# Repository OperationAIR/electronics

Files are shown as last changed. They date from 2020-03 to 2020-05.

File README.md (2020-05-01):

# Electronics and firmware for Operation Air Ventilator

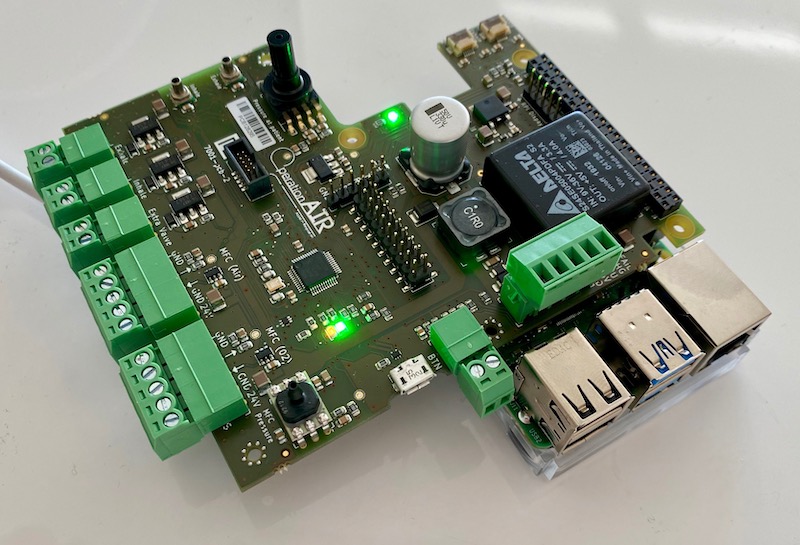
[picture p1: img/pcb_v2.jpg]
OperationAir PCB


The electronics for the Operation Air AIROne is comprised of a custom developed PCB with a LPC11U37 microcontroller stacked on top of a Raspberry Pi 4 (Model B).

This repository contains the electronic designs for the PCB and the accompanying firmware.

The Pi talks to the microcontroller over UART using a [custom binary protocol](firmware/README.md#uart-communication-protocol).

Contact info@interay.com for assembled, tested and programmed ready for use boards.

## License

Copyright (c) 2020 TU Delft. All rights reserved.

Licensed under the [Apache 2.0](LICENSE) license.

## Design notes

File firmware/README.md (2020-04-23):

# Operation Air embedded firmware

The firmware runs on a LPC11U37 microcontroller.

## Requirements

* [Gnu Arm Embedded Toolchain](https://developer.arm.com/open-source/gnu-toolchain/gnu-rm/downloads)
* CMake
* JTAG/SWD programmer, such as the [Black Magic Probe](https://github.com/blacksphere/blackmagic/wiki) (BMP) , or any OpenOCD compatible device.

## Build

First we need to create a `config.cmake` file in which we can configure our build

```console
cp config.cmake.example config.cmake
```

In `config.cmake` we can configure the BMP if we're using any. On MacOS that would look like:

```
set(BLACKMAGIC_DEV /dev/cu.usbmodemC1DDCDF81)
```

Next we need to create a `build` directory in the project root and run CMake to fetch all dedpendencies and create the makefiles.

```console
mkdir build
cd build
cmake ..
```

The previous part only needs to be done the first time.
Now we're ready to actually compile the project. Inside the `build` directory run

```console
make
```

And to flash

```console
make flash
```

## UART Communication Protocol

The microcontroller communicates with a Raspberry Pi over `uart`. The PCB is designed as a Raspberry Pi Hat and uses the `TXD` and `RXD` pins in the Raspberry Pi header. Note that `Rx` and `Tx` are swapped on the microcontroller side.

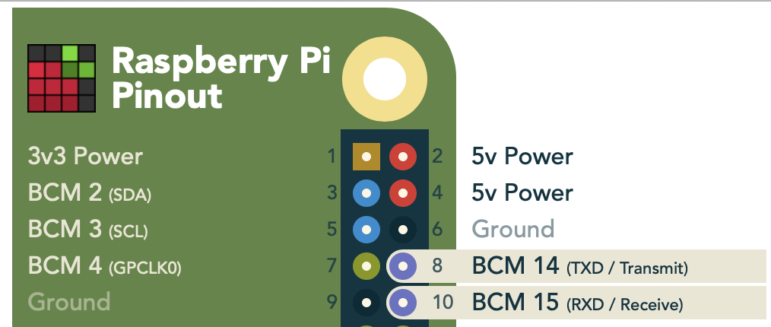
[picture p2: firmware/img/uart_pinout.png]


A binary protocol is used where each command is a unique 32 bit integer (sent LSB first) followed by an optional payload.

The baudrate is `500000`.

Binary responses from the microcontroller for the specific command are also prefixed with the same 4 bytes. ASCII responses, for logging or debug puposes are prefixed with `0x23232323` ('####') and end in a newline `\n` character.

### Command Overview

| Command             | Description                             | Prefix     | Payload      | Response         |
| -------------       |---------------------------------------- | ---------: | ------------ | --------         |
| NewSettings         | Send and apply new operation settings   | `0x41424344` | [Settings](#Settings)   | Applied Settings |
| RequestSettings     | Request current settings                | `0x45464748` | None         | [Settings](#Settings-Response) |
| RequestSensorValues | Request current samples for all sensors | `0x0D15EA5E` | None         | [Sensor Values](#Sensor-Values-Response)    |
| InspiratoryHoldStart| Trigger inspiratory hold if breathing is started | `0x99998888` | None| Log info (ascii) |
| InspiratoryHoldStop | Stop inspiratory hold                   | `0x99999999` | None         | Log info (ascii) |
| ExpiratoryHoldStart | Trigger expiratory hold if breathing is started | `0x77776666` | None | Log info (ascii) |
| ExpiratoryHoldStop  | Stop expiratory hold                    | `0x77777777` | None         | Log info (ascii) |
| StatusLedOn         | Turn on status LED (Green)              | `0x55551111` | None         | Log info (ascii) |
| StatusLedOff        | Turn off status LED (Green)             | `0x55661111` | None         | Log info (ascii) |
| ErrorLedOn          | Turn on error LED (Red)                 | `0x55552222` | None         | Log info (ascii) |
| ErrorLedOff         | Turn off error LED (Red)                | `0x55662222` | None         | Log info (ascii) |
| SwitchExhaleOn      | Turn on 24V switch for exhale           | `0x66663333` | None         | Log info (ascii) |
| SwitchExhaleOff     | Turn off 24V switch for exhale          | `0x66773333` | None         | Log info (ascii) |
| SwitchInhaleOn      | Turn on 24V switch for inhale           | `0x66664444` | None         | Log info (ascii) |
| SwitchInhaleOff     | Turn off 24V switch for ihale           | `0x66774444` | None         | Log info (ascii) |
| SwitchExtraOn       | Turn on 24V switch (extra)              | `0x66665555` | None         | Log info (ascii) |
| SwitchExtraOff      | Turn off 24V switch (extra)             | `0x66775555` | None         | Log info (ascii) |
| MFCAirSet           | Set 12 bit analog value for MFC (Air)   | `0x77771111` | [uint16 (mV)](#MFC-set-point) | Log info (ascii) |
| MFCAirGet           | Get analog MFC (Air) feedback value     | `0x77881111` | None         | [MFC Feedback uint16 (mV)](#MFC-analog-in)  |
| MFCO2Set            | Set 12 bit analog value for MFC (O2)    | `0x77772222` | [uint16 (mV)](#MFC-set-point) | Log info (ascii) |
| MFCO2Get            | Get analog MFC (O2) feedback value      | `0x77882222` | None         | [MFC Feedback uint16 (mV)](#MFC-analog-in)  |
| UserSwitchGet       | Get current user switch status (0 or 1) | `0x88883333` | None         | 0 or 1 (ascii)   |

### Settings

Settings is defined as a struct where each entry is a 16 bit unsigned integer.

```
typedef struct __attribute__((packed)) {
    uint16_t start; // breathing is started
    uint16_t peep; // exhale pressure
    uint16_t frequency; // breathing cycles per minute
    uint16_t ratio; // ratio between inhale exhale
    uint16_t pressure; // inhale pressure
    uint16_t oxygen; // oxygen percentage for mixer
    uint16_t max_pressure_alarm;
    uint16_t min_pressure_alarm;
    uint16_t max_TV_alarm;
    uint16_t min_TV_alarm;
    uint16_t max_fiO2_alarm;
    uint16_t min_fiO2_alarm;
    uint16_t crc;
} OperationSettings;
```

The final entry is a `crc16 usb` checksum with the following specs:

```
CRC16 USB
Poly: 0x8005
Init: 0xFFFF
RefIn: True
RefOut: True
XorOut: 0xFFFF
```

### Sensor Values Response

From microcontroller to host.
Sensor values are prefixed with the 32-bit little-endian value `0x0D15EA5E` and followed by a crc16 usb checksum. The sensor data is a struct of 32bit signed integers:

The total data packet is then `4 + (15 x 4) + 2 = 66 bytes`

```
struct SensorsAllData {
    int32_t flow_inhale;            // Inhale flow [mL / minute] (approximation)
    int32_t flow_exhale;            // Exhale flow [mL / minute]

    int32_t pressure_inhale;        // Inhale pressure [Pa]
    int32_t pressure_exhale;        // Exhale pressure [Pa]
    int32_t pressure_patient;       // Pressure at patient [Pa] (TODO: Not Implemented Yet)
    int32_t pressure_mfc;           // Pressure at MFC pressure vessel [Pa]

    int32_t oxygen;                 // Oxygen percentage [0-100]
    int32_t tidal_volume_inhale;    // Tidal volume [mL] (Based on inhale flow)
    int32_t tidal_volume_exhale;    // Tidal volume [mL] (Based on exhale flow)
    int32_t minute_volume;          // Average flow (exhale) [mL / minute] (average over last 10 sec interval)
    int32_t cycle_state;            // PeeP / Peak / None
    int32_t power_status;           // UPS status [mV OR-ed with UPSStatus bits]

    int32_t inspiratory_hold_result;// Value for end of inspiratory hold mean sensors
    int32_t expiratory_hold_result; // Value for end of expiratory hold mean sensors

    uint32_t system_status;         // enum SystemStatus value(s) OR-ed together

}
```

The power_status field shows the measured power voltage in mv, OR-combined with one
of these status flags:
```
enum UPSStatus {
    UPS_STATUS_UNKNOWN              = (0),
    UPS_STATUS_OK                   = (1 << 31),
    UPS_STATUS_BATTERY_POWERED      = (1 << 30),
    UPS_STATUS_FAIL                 = (1 << 29)
};

```

The system_status field shows multiple OR-combined flags indicating the status
of the electronics, including errors that have occurred. In normal operation,
only the flag `SYSTEM_STATUS_BOOT_POWER_ON` (or `SYSTEM_STATUS_BOOT_RESET_BY_PI` after a firmware upgrade) is expected to be set. Flags are only cleared by a resetting the MCU: a flag being set means that the error has occurred at least once since the last reset.
```
enum SystemStatus {
    SYSTEM_STATUS_UNKNOWN               = 0,

    // Boot info: one of these should be set at boot
    SYSTEM_STATUS_BOOT_POWER_ON         = (1 << 0),     // Power-On-Reset
    SYSTEM_STATUS_BOOT_RESET_BY_PI      = (1 << 1),     // External reset (triggered by RPI)
    SYSTEM_STATUS_BOOT_RESET_BY_ERROR   = (1 << 2),     // Watchdog reset (firmware bug)
    SYSTEM_STATUS_BOOT_RESET_BY_PWR_FAIL= (1 << 3),     // BOD reset (3.3V unstable)
    SYSTEM_STATUS_BOOT_RESET_BY_UNKNOWN = (1 << 4),     // SYSRST or unknown

    // Errors in sensors or actuators:
    SYSTEM_STATUS_ERROR_SENSOR_P_INSP   = (1 << 5),     // Inspiration pressure sensor error
    SYSTEM_STATUS_ERROR_SENSOR_P_EXP    = (1 << 6),     // Expiration pressure sensor error
    SYSTEM_STATUS_ERROR_SENSOR_P_PATIENT= (1 << 7),     // Patient pressure sensor error
    SYSTEM_STATUS_ERROR_SENSOR_FLOW     = (1 << 8),     // Flow sensor error

    SYSTEM_STATUS_ERROR_ACTUATOR_MFC_AIR= (1 << 16),    // Air MFC (DAC) error
    SYSTEM_STATUS_ERROR_ACTUATOR_MFC_O2 = (1 << 17),    // O2 MFC (DAC) error

    SYSTEM_STATUS_ERROR_MFC_OVERPRESSURE= (1 << 18),    // MFC output pressure too high

    // NOTE: new status flags may be added here
    //

    // Generic errors
    SYSTEM_STATUS_ERROR_EEPROM          = (1 << 29),    // EEPROM error: settings may not be remembered after reset
    SYSTEM_STATUS_ERROR_I2C_BUS         = (1 << 30),    // I2C bus is in invalid state

    // Warning: the firmware is not a release build
    SYSTEM_STATUS_DEBUG_ENABLED         = (1 << 31),    // Debug build should not be released
};

```

### Settings Response

From microcontroller to host.
Settings are prefixed with the 32-bit little-endian value: `0x41424344`, followed by the [Settings](#Settings).

### MFC set point

Set point for the mass flow controller. The MFC is controlled through a 12bit i2c DAC. The payload for the MFC set command accepts a unsigned 16 bit integer between 0 and 4095.

### MFC analog in

Feedback from the MFC are returned as uint16 value in millivolts (0-5000). Note: this command is binary and is not terminated with '\n'.

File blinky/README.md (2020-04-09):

# Operation Air embedded firmware

The firmware runs on a LPC11U37 microcontroller.

## Requirements

* [Gnu Arm Embedded Toolchain](https://developer.arm.com/open-source/gnu-toolchain/gnu-rm/downloads)
* CMake
* JTAG/SWD programmer, such as the [Black Magic Probe](https://github.com/blacksphere/blackmagic/wiki) (BMP) , or any OpenOCD compatible device.

## Build

First we need to create a `config.cmake` file in which we can configure our build

```console
cp config.cmake.example config.cmake
```

In `config.cmake` we can configure the BMP if we're using any. On MacOS that would look like:

```
set(BLACKMAGIC_DEV /dev/cu.usbmodemC1DDCDF81)
```

Next we need to create a `build` directory in the project root and run CMake to fetch all dedpendencies and create the makefiles.

```console
mkdir build
cd build
cmake ..
```

The previous part only needs to be done the first time.
Now we're ready to actually compile the project. Inside the `build` directory run

```console
make
```

And to flash

```console
make flash
```

## UART Communication Protocol

The microcontroller communicates with a Raspberry Pi over `uart`. The PCB is designed as a Raspberry Pi Hat and uses the `TXD` and `RXD` pins in the Raspberry Pi header. Note that `Rx` and `Tx` are swapped on the microcontroller side.



A binary protocol is used where each command is a unique 32 bit integer (sent LSB first) followed by an optional payload.

The baudrate is `500000`.

Binary responses from the microcontroller for the specific command are also prefixed with the same 4 bytes. ASCII responses, for logging or debug puposes are prefixed with `0x23232323` ('####') and end in a newline `\n` character.

### Command Overview

| Command             | Description                             | Prefix     | Payload      | Response         |
| -------------       |---------------------------------------- | ---------: | ------------ | --------         |
| NewSettings         | Send and apply new operation settings   | `0x41424344` | [Settings](#Settings)   | Applied Settings |
| RequestSettings     | Request current settings                | `0x45464748` | None         | [Settings](#Settings-Response) |
| RequestSensorValues | Request current samples for all sensors | `0x0D15EA5E` | None         | [Sensor Values](#Sensor-Values-Response)    |
| InspiratoryHoldStart| Trigger inspiratory hold if breathing is started | `0x99998888` | None| Log info (ascii) |
| InspiratoryHoldStop | Stop inspiratory hold                   | `0x99999999` | None         | Log info (ascii) |
| ExpiratoryHoldStart | Trigger expiratory hold if breathing is started | `0x77776666` | None | Log info (ascii) |
| ExpiratoryHoldStop  | Stop expiratory hold                    | `0x77777777` | None         | Log info (ascii) |
| StatusLedOn         | Turn on status LED (Green)              | `0x55551111` | None         | Log info (ascii) |
| StatusLedOff        | Turn off status LED (Green)             | `0x55661111` | None         | Log info (ascii) |
| ErrorLedOn          | Turn on error LED (Red)                 | `0x55552222` | None         | Log info (ascii) |
| ErrorLedOff         | Turn off error LED (Red)                | `0x55662222` | None         | Log info (ascii) |
| SwitchExhaleOn      | Turn on 24V switch for exhale           | `0x66663333` | None         | Log info (ascii) |
| SwitchExhaleOff     | Turn off 24V switch for exhale          | `0x66773333` | None         | Log info (ascii) |
| SwitchInhaleOn      | Turn on 24V switch for inhale           | `0x66664444` | None         | Log info (ascii) |
| SwitchInhaleOff     | Turn off 24V switch for ihale           | `0x66774444` | None         | Log info (ascii) |
| SwitchExtraOn       | Turn on 24V switch (extra)              | `0x66665555` | None         | Log info (ascii) |
| SwitchExtraOff      | Turn off 24V switch (extra)             | `0x66775555` | None         | Log info (ascii) |
| MFCAirSet           | Set 12 bit analog value for MFC (Air)   | `0x77771111` | [uint16 (mV)](#MFC-set-point) | Log info (ascii) |
| MFCAirGet           | Get analog MFC (Air) feedback value     | `0x77881111` | None         | [MFC Feedback (mV)](#MFC-analog-in)  |
| MFCO2Set            | Set 12 bit analog value for MFC (O2)    | `0x77772222` | [uint16 (mV)](#MFC-set-point) | Log info (ascii) |
| MFCO2Get            | Get analog MFC (O2) feedback value      | `0x77882222` | None         | [MFC Feedback (mV)](#MFC-analog-in)  |
| UserSwitchGet       | Get current user switch status (0 or 1) | `0x88883333` | None         | 0 or 1 (ascii)   |

### Settings

Settings is defined as a struct where each entry is a 16 bit unsigned integer.

```
typedef struct __attribute__((packed)) {
    uint16_t start; // breathing is started
    uint16_t peep; // exhale pressure
    uint16_t frequency; // breathing cycles per minute
    uint16_t ratio; // ratio between inhale exhale
    uint16_t pressure; // inhale pressure
    uint16_t oxygen; // oxygen percentage for mixer
    uint16_t max_pressure_alarm;
    uint16_t min_pressure_alarm;
    uint16_t max_TV_alarm;
    uint16_t min_TV_alarm;
    uint16_t max_fiO2_alarm;
    uint16_t min_fiO2_alarm;
    uint16_t crc;
} OperationSettings;
```

The final entry is a `crc16 usb` checksum with the following specs:

```
CRC16 USB
Poly: 0x8005
Init: 0xFFFF
RefIn: True
RefOut: True
XorOut: 0xFFFF
```

### Sensor Values Response

From microcontroller to host.
Sensor values are prefixed with the 32-bit little-endian value `0x0D15EA5E` and followed by a crc16 usb checksum. The sensor data is a struct of 32bit signed integers:

The total data packet is then `4 + (14 x 4) + 2 = 62 bytes`

```
struct SensorsAllData {
    int32_t flow_inhale;        // Inhale flow [mL / minute] (approximation)
    int32_t flow_exhale;        // Exhale flow [mL / minute]

    int32_t pressure_inhale;    // Inhale pressure [Pa]
    int32_t pressure_exhale;    // Exhale pressure [Pa]
    int32_t pressure_patient;   // Pressure at patient [Pa] (TODO: Not Implemented Yet)
    int32_t pressure_mfc;       // Pressure at MFC pressure vessel [Pa]

    int32_t oxygen;             // Oxygen percentage [0-100]
    int32_t tidal_volume_inhale;       // Tidal volume [mL] (Based on inhale flow)
    int32_t tidal_volume_exhale;       // Tidal volume [mL] (Based on exhale flow)
    int32_t minute_volume;      // Average flow (exhale) [mL / minute] (average over last 10 sec interval)
    int32_t cycle_state;        // PeeP / Peak / None
    int32_t power_status;       // UPS status [mV OR-ed with UPSStatus bits]

    int32_t inspiratory_hold_result;   // Value for end of inspiratory hold mean sensors
    int32_t expiratory_hold_result;   // Value for end of expiratory hold mean sensors

}
```

The power_status field shows the measured power voltage in mv, OR-combined with one
of these status flags:
```
enum UPSStatus {
    UPS_STATUS_UNKNOWN              = (0),
    UPS_STATUS_OK                   = (1 << 31),
    UPS_STATUS_BATTERY_POWERED      = (1 << 30),
    UPS_STATUS_FAIL                 = (1 << 29)
};

```

### Settings Response

From microcontroller to host.
Settings are prefixed with the 32-bit little-endian value: `0x41424344`, followed by the [Settings](#Settings).

### MFC set point

Set point for the mass flow controller. The MFC is controlled through a 12bit i2c DAC. The payload for the MFC set command accepts a unsigned 16 bit integer between 0 and 4095.

### MFC analog in

Analog-in scaled to millivolts as int32

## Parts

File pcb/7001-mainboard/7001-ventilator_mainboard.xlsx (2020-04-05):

Sync | Ref | Qty | Value | Footprint | MPN | Farnell | Mouser | Digikey
1 | R16, R17, R8, R9, | 4 | 0 | Resistor_SMD:R_0805_2012Metric |  | 2447574
1 | R5, R4, | 2 | 33R | Resistor_SMD:R_0805_2012Metric |  | 2447640
1 | R49, R50, R41, R42, R43, | 5 | 150 | Resistor_SMD:R_0805_2012Metric |  | 2747563
1 | R3, R12, R22, R24, R23, | 5 | 1k5 | Resistor_SMD:R_0805_2012Metric |  | 2447592
1 | R29, R40, R38, R19, R44, R37, R46, R45, | 8 | 3.3k | Resistor_SMD:R_0805_2012Metric |  | 2447651
1 | R34, R36, R32, R21, | 4 | 4.7k | Resistor_SMD:R_0805_2012Metric |  | 2447672
1 | R47, | 1 | 150 1% | Resistor_SMD:R_0805_2012Metric
1 | R48, | 1 | 2.32k 1% | Resistor_SMD:R_0805_2012Metric
 | ~~R48,~~ | ~~1~~ | ~~2.2k~~ | ~~Resistor_SMD:R_0805_2012Metric~~
1 | RV1, | 1 | Varistor | Jitter_Footprints:WE_VS_Varistor | 82551250
1 | R6, R35, R39, R15, R18, R11, | 6 | 10k | Resistor_SMD:R_0805_2012Metric |  | 2447553
1 | R31, R10, R1, R2, | 4 | 68k | Resistor_SMD:R_0805_2012Metric |  | 2447706
1 | R33, R14, R20, R13, | 4 | 100k | Resistor_SMD:R_0805_2012Metric |  | 2447551
1 | C10, C12, | 2 | 18pF | Capacitor_SMD:C_0805_2012Metric |  | 2821165
1 | C34, | 1 | 470pF | Capacitor_SMD:C_0805_2012Metric |  | 2409053
1 | C40, C20, C7, C35, C37, | 5 | 2.2nF | Capacitor_SMD:C_0805_2012Metric |  | 1414681
1 | C5, C6, C36, | 3 | 1nF | Capacitor_SMD:C_0805_2012Metric |  | 3013468
1 | C17, C45, C27, | 3 | 2.2nF 50V | Capacitor_SMD:C_0805_2012Metric |  | 1414681
1 | C46, C47, | 2 | 10nF 100V | Capacitor_SMD:C_1206_3216Metric | 885012208112
1 | C28, C29, C1, C23, C49, C2, C3, C21, C15, C50, C43, C8, C9, C31, C33, | 15 | 100nF | Capacitor_SMD:C_0805_2012Metric |  | 1650866
1 | C19, C39, C48, C51, C54, | 5 | 100nF 50V | Capacitor_SMD:C_0805_2012Metric |  | 1650866
1 | C11, C4, C52, C30, C32, | 5 | 1uF | Capacitor_SMD:C_0805_2012Metric |  | 2688485
1 | C13, | 1 | 4.7uF | Capacitor_SMD:C_0805_2012Metric |  | 2346968
1 | C25, C16, C53, | 3 | 10uF | Capacitor_SMD:C_0805_2012Metric |  | 3013485
1 | C38, C18, C42, C44, C41, C24, C14, C26, | 8 | 10uF 50V | Capacitor_SMD:C_1210_3225Metric |  | 2834943
1 | C22, | 1 | 330uF | Jitter_Footprints:CP_Elec_12.5_MAL214699107E3 | MAL214699107E3 | 2859824
1 | D1, D2, D11, | 3 | D_Schottky | Diode_SMD:D_SOD-123F | NRVTS245ESFT3G | 3003750
1 | D3, | 1 | S5MB R5G 100V | Diode_SMD:D_SMB | S5MB R5G
1 | D4, | 1 | D_TVS | Jitter_Footprints:WE-TVSP_TVS_DIODE | 824501301 | 2536572
1 | D7, D6, D5, D8, D9, | 5 | Green | LED_SMD:LED_0805_2012Metric | KP-2012LSGC | 2463991
1 | D10, | 1 | Red | LED_SMD:LED_0805_2012Metric | KPT-2012EC | 2099236
1 | FB1, FB2, | 2 | BLM18HE601SN1D | Inductor_SMD:L_0603_1608Metric | BLM18HE601SN1D | 2443238
1 | FL1, | 1 | 744282010 | Jitter_Footprints:L_CommonMode_Wuerth_WE-SCC | 744282010
1 | J1, | 1 | USB_B_Micro | Jitter_Footprints:USB_Micro-B_Molex_47346-0001 | 47346-0001 | 1568026
1 | J5, | 1 | 5-pin screw terminal vertical | Jitter_Footprints:TerminalBlock_Wurth_WR-TBL_691321100005_1x05_P3.50mm_Vertical | 691321100005
 | ~~J5,~~ | ~~1~~ | ~~2-pin screw terminal~~ | ~~Jitter_Footprints:TerminalBlock_Wurth_WR-TBL_691321100005_1x05_P3.50mm_Vertical~~ | ~~691321100005~~
 | ~~J5,~~ | ~~0~~ | ~~2-pin screw terminal~~ | ~~Jitter_Footprints:TerminalBlock_Wurth_WR-TBL_691322110008_1x08_P3.50mm_Horizontal~~ | ~~691322110008~~
1 | J13, J14, J4, J3, | 4 | 2-pin screw terminal | Jitter_Footprints:TerminalBlock_Wurth_WR-TBL_691322110002_1x02_P3.50mm_Horizontal | 691322110002 | 1841315
1 | J6, | 1 | 5V out | Connector_PinHeader_2.54mm:PinHeader_1x05_P2.54mm_Vertical
1 | J2, J7, | 2 | 6-pin FFC connector | Jitter_Footprints:Hirose_FH12-6S-0.5SH_1x06-1MP_P0.50mm_Horizontal | FH12-6S-0.5SH | 1324538
1 | J9, | 1 | Raspberry_Pi_2_3 | Jitter_Footprints:PinSocket_2x20_P2.54mm_Vertical_holes_SMD | REF-182665-01 | 2827937
1 | J10, | 1 | 6-pin header | Connector_PinHeader_2.54mm:PinHeader_1x06_P2.54mm_Vertical
1 | J11, J8, | 2 | 5-pin screw terminal | Jitter_Footprints:TerminalBlock_Wurth_WR-TBL_691322110005_1x05_P3.50mm_Horizontal | 691322110005 | 1841318
 | ~~J11, J8,~~ | ~~2~~ | ~~2-pin screw terminal~~ | ~~Jitter_Footprints:TerminalBlock_Wurth_WR-TBL_691322110005_1x05_P3.50mm_Horizontal~~ | ~~691322110005~~ | 1841318
1 | J15, | 1 | 2x10-pin header | Connector_PinHeader_2.54mm:PinHeader_2x10_P2.54mm_Vertical_SMD | 61032021121
1 | J16, | 1 | 10-pin SWD header | Jitter_Footprints:connector_jtag_10pin_shrouded | 20021521-00010T1LF
1 | Q1, | 1 | NX3020NAKV,115 | Package_TO_SOT_SMD:SOT-666 | NX3020NAKV,115 | 2311182
1 | U1, U8, | 2 | MPRLS0001PG0000SA | Jitter_Footprints:MPRLS0001PG0000SA | MPRLS0001PG0000SA |  |  | 480-7100-1-ND
1 | U2, | 1 | TPD2E2U06 | Package_TO_SOT_SMD:SOT-553 | TPD2E2U06DRLR | 3116500
1 | U3, | 1 | LPC11U37FBD48-401_ | Package_QFP:LQFP-48_7x7mm_P0.5mm | LPC11U37FBD48/401 | 2115662
1 | U4, | 1 | MCP1825S-3302E | Package_TO_SOT_SMD:SOT-223-3_TabPin2 | MCP1825S-3302E | 1578404
1 | U5, | 1 | S24SE05004PDFA_DC-DC | Jitter_Footprints:DCDC-5V_S24SE05004PDFA | S24SE05004PDFA |  | 108-S24SE05004PDFA
1 | U6, U15, | 2 | MCP4725 | Package_TO_SOT_SMD:SOT-23-6 | MCP4725A1T-E/CH | 2774927
1 | U9, | 1 | ABPDXXX000XXAX5 | Jitter_Footprints:ABPDXXX000XX0XX | ABPDANT015PGAA5
1 | U11, | 1 | MPVZ5010GW6U | Jitter_Footprints:MPVZ5010GW6U | MPVZ5010GW6U |  | 841-MPVZ5010GW6U | 568-13502-ND
1 | U13, U14, U7, | 3 | ITS4142NHUMA1 | Package_TO_SOT_SMD:SOT-223 | ITS4142NHUMA1 | 1440816
1 | U16, | 1 | LD1086DTTR | Jitter_Footprints:TO-252-2 | LD1086DTTR (adjustable)
1 | Y1, | 1 | 12MHz | Crystal:Crystal_SMD_3225-4Pin_3.2x2.5mm | 7M-12.000MEEQ-T | 2308719
 | Non-pcb parts
 | K3, K4, K13, K14 | 4 | 2 way straight | Mates with 691322110002 | 691361100002 |  |  | 732-2751-ND
 | K5, K11, K8 | 3 | 5 way straight |  | 691361100005 |  |  | 732-2754-ND
 | K9 | 1 | 20-pin tussenheader RPI | wordt tijdens assemblage tussen pcb en RPI geplaatst | REF-182683-02

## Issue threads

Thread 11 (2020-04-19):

### ISSUE TITLE
MFC feedback analog in werkt soms niet

### ISSUE THREAD

**Issue by ijager** [OperationAIR/electronics#11]
Interay meldt dat de analoge inputs voor de MFC's soms geen response geven op de testcommando's

**Comment by sjorsdewit** [comment]
lijkt gewoon te werken? Valt wel op dat ons eigen terminal programma de response niet weergeeft totdat je een ander commando uitvoert dat text-mode is (eindigend op \n)

**Comment by sjorsdewit** [comment]
boardconfig ten tijde van productietest was ook nog niet correct (ADC channels verwisseld). dit zal waarschijnlijk de oorzaan zijn geweest.

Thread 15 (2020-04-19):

### ISSUE TITLE
Settings validation: what should the bounds be?

### ISSUE THREAD

**Issue by sjorsdewit** [OperationAIR/electronics#15]
Each of these settings from the RPI are validated on the MCU:
- PEEP
- frequency
- peak pressure
- ratio
- oxygen

As a safety feature, the MCU ignores a set of new settings if any of them is outside a valid range (see settings.c). But what should the range of each setting be?

The current bounds may not be in agreement with the GUI, which could lead to confusion for the end-user when they are not applied..

**Comment by ijager** [comment]
Uit de feedback kwam deze tabel:

  | Default waarde | Range | Stapgrootte waarde en alarm | Alarm range default
-- | -- | -- | -- | --
PEEP [cmH2O] | 10 | 5 - 30 | 1 | 8 - 12
PC boven PEEP [cmH2O] | 15 | 5 - 40 | 2 | 20 - 30
Freqentie [/min] | 15 | 5 - 40 | 1 | -
FiO2 [%O2] | 40 | 21 - 100 | 5 | 35 - 45
I:E | 1:2 | 1:1 - 1:3 | -:0.5 | -
TV [ml] | - | - | 50 | 300 - 700
Mve [L/min] | - | - | 0.5 | 5 - 9

**Comment by sjorsdewit** [comment]
Implemented in 99f8ec7f

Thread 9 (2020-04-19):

### ISSUE TITLE
Flowsensor: geen error waarde

### ISSUE THREAD

**Issue by ijager** [OperationAIR/electronics#9]
Ze kunnen in friesland geen verschil zien tussen 0 flow of geen sensor aangesloten. Dus dit is een probleem voor het testen

**Comment by sjorsdewit** [comment]
flowsensor zou -1 moeten geven bij fout. Daarnaast is de[ system status](https://github.com/OperationAIR/electronics/blob/master/firmware/README.md#sensor-values-response) beschikbaar

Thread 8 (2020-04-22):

### ISSUE TITLE
Drop pressure in MFC buffer after opening pressure relieve valve.

### ISSUE THREAD

**Issue by hubaldv** [OperationAIR/electronics#8]
If pressure in buffer is > 1000mbar, pressure relief valve is opened. This valve closes if pressure is <500 or <600 mbar. The software should detect that the valve is opened and let the pressure in the buffer drop below this limit such that the valve will close again.

**Comment by sjorsdewit** [comment]
Implemented in dbf1174faa512ad56f234c90fe79aa9329e03858

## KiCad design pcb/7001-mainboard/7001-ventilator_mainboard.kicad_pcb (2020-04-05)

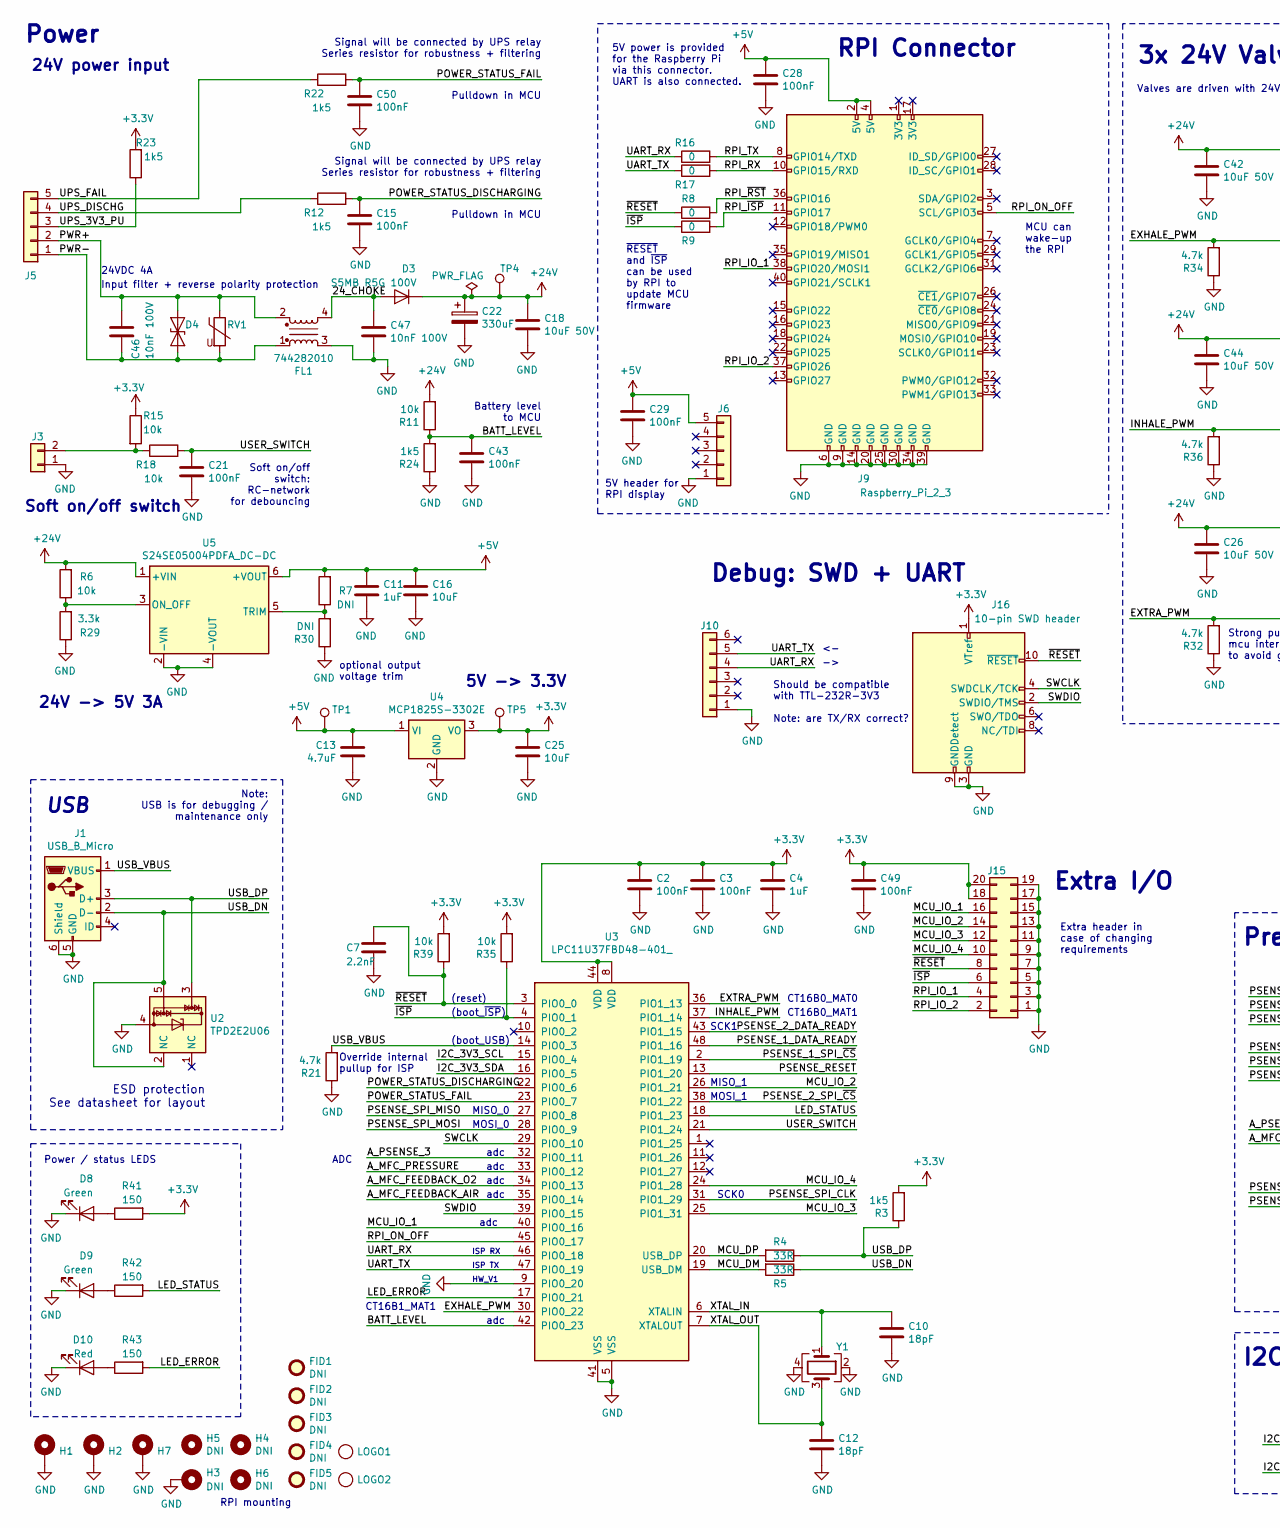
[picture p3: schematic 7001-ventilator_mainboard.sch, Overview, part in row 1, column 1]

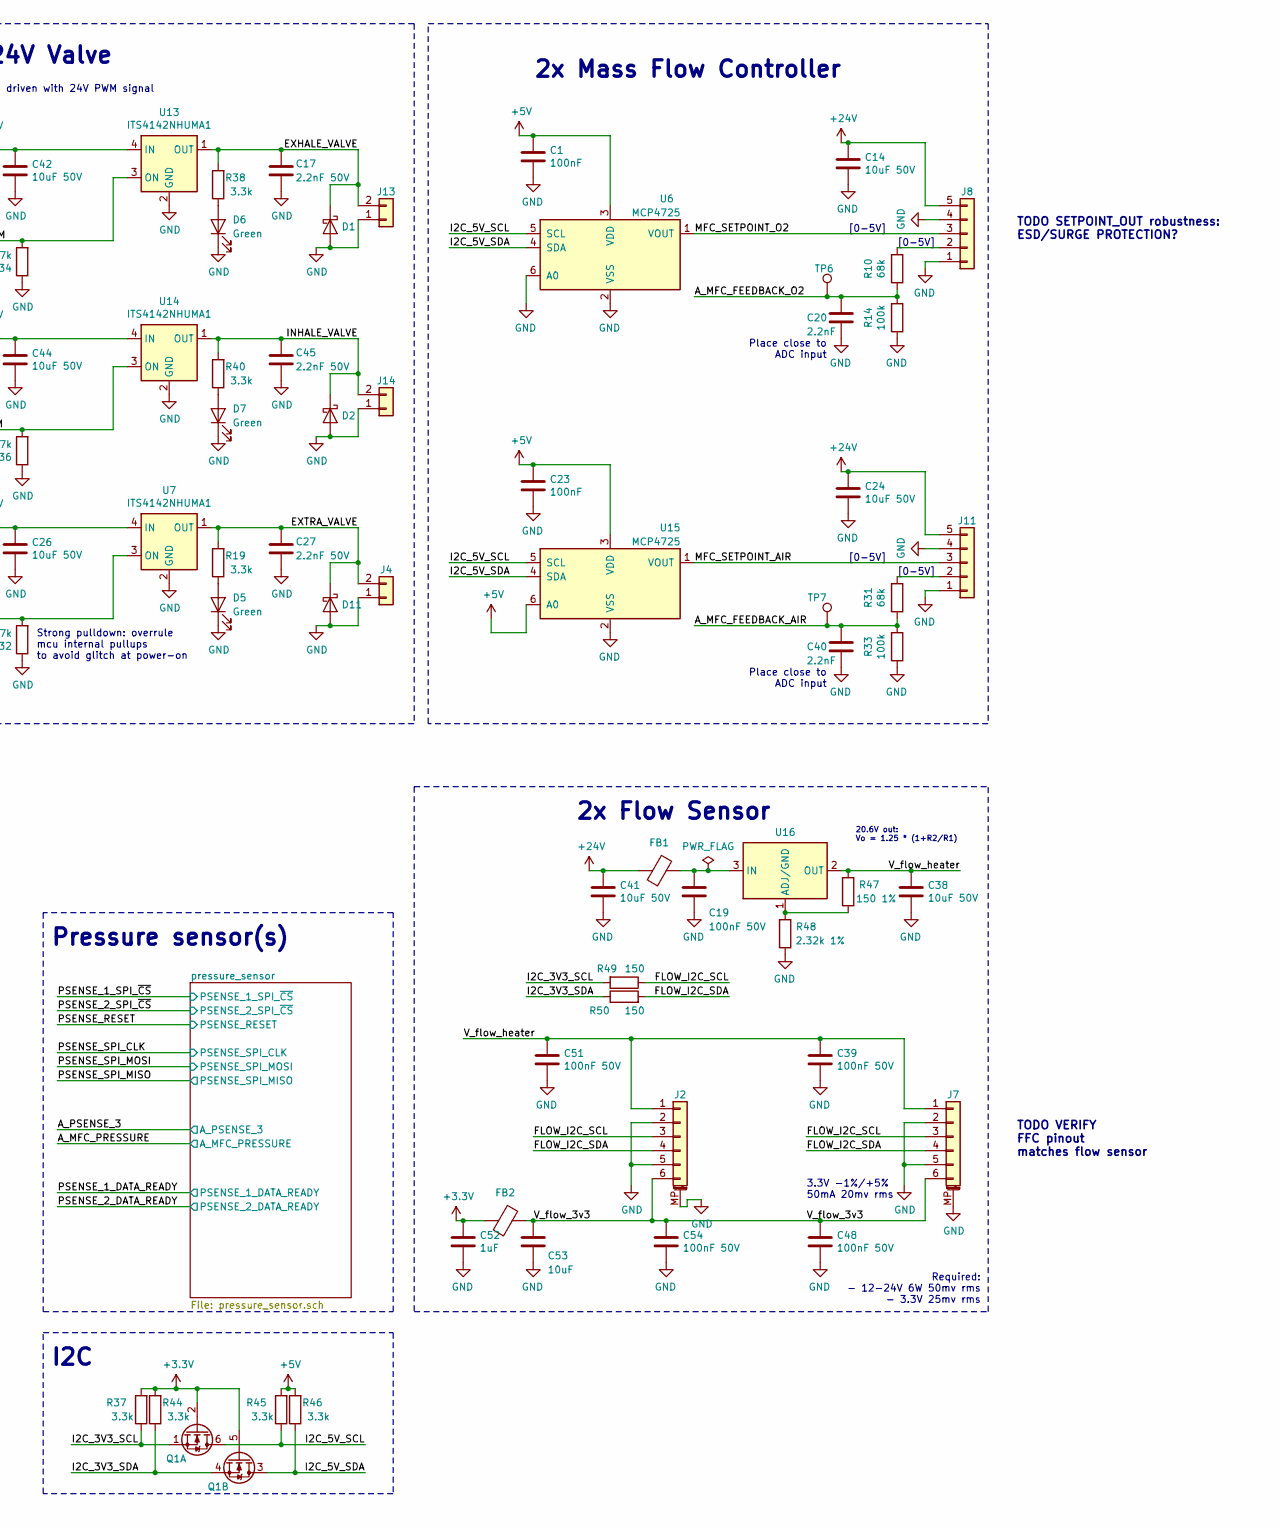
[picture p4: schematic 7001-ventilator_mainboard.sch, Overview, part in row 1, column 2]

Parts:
C1, C2, C3, C15, C21, C23, C28, C29, C43, C49, C50: 100nF; C_0805_2012Metric
C4, C11, C52: 1uF; C_0805_2012Metric
C7, C20, C40: 2.2nF; C_0805_2012Metric
C10, C12: 18pF; C_0805_2012Metric
C13: 4.7uF; C_0805_2012Metric
C14, C18, C24, C26, C38, C41, C42, C44: 10uF 50V; C_1210_3225Metric
C16, C25, C53: 10uF; C_0805_2012Metric
C17, C27, C45: 2.2nF 50V; C_0805_2012Metric
C19, C39, C48, C51, C54: 100nF 50V; C_0805_2012Metric
C22: 330uF; CP_Elec_12.5_MAL214699107E3; MPN MAL214699107E3
C46, C47: 10nF 100V; C_1206_3216Metric; MPN 885012208112
D1, D2, D11: D_Schottky; D_SOD-123F; MPN NRVTS245ESFT3G
D3: S5MB R5G 100V; D_SMB; MPN S5MB R5G
D4: D_TVS; WE-TVSP_TVS_DIODE; MPN 824501301; Farnell 2536572
D5, D6, D7, D8, D9: Green; LED_0805_2012Metric; MPN KP-2012LSGC; Farnell 2463991
D10: Red; LED_0805_2012Metric; MPN KPT-2012EC; Farnell 2099236
FB1, FB2: BLM18HE601SN1D; L_0603_1608Metric; MPN BLM18HE601SN1D; Farnell 2443238
FID1, FID2, FID3, FID4, FID5: DNI; Fiducial_1mm_Mask2mm
FL1: 744282010; L_CommonMode_Wuerth_WE-SCC; MPN 744282010
H1, H2, H7: DNI (mounting hole); MountingHole_2.7mm_M2.5_Pad__wavesolder
H3: DNI; MountingHole_2.7mm_M2.5_Pad__wavesolder
H4, H5, H6: DNI; MountingHole_2.7mm_M2.5__wavesolder
J1: USB_B_Micro; USB_Micro-B_Molex_47346-0001; MPN 47346-0001; Farnell 1568026
J2, J7: 6-pin FFC connector; Hirose_FH12-6S-0.5SH_1x06-1MP_P0.50mm_Horizontal; MPN FH12-6S-0.5SH; Farnell 1324538
J3, J4, J13, J14: 2-pin screw terminal; TerminalBlock_Wurth_WR-TBL_691322110002_1x02_P3.50mm_Horizo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; MPN 691322110002; Farnell 1841315
J5: 5-pin screw terminal vertical; TerminalBlock_Wurth_WR-TBL_691321100005_1x05_P3.50mm_Vertic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; MPN 691321100005
J6: 5V out; PinHeader_1x05_P2.54mm_Vertical
J8, J11: 5-pin screw terminal; TerminalBlock_Wurth_WR-TBL_691322110005_1x05_P3.50mm_Horizo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; MPN 691322110005
J9: Raspberry_Pi_2_3; PinSocket_2x20_P2.54mm_Vertical_holes_SMD; MPN REF-182665-01
J10: 6-pin header; PinHeader_1x06_P2.54mm_Vertical
J15: 2x10-pin header; PinHeader_2x10_P2.54mm_Vertical_SMD; MPN 61032021121
J16: 10-pin SWD header; connector_jtag_10pin_shrouded; MPN 20021521-00010T1LF
LOGO1: LOGO; JitterLogo
LOGO2: LOGO; OperationAir260
Q1: NX3020NAKV,115; SOT-666; MPN NX3020NAKV,115; Farnell 2311182
R3, R12, R22, R23, R24: 1k5; R_0805_2012Metric
R4, R5: 33R; R_0805_2012Metric
R6, R11, R15, R18, R35, R39: 10k; R_0805_2012Metric
R7, R30: DNI; R_0805_2012Metric
R8, R9, R16, R17: 0; R_0805_2012Metric
R10, R31: 68k; R_0805_2012Metric
R14, R33: 100k; R_0805_2012Metric
R19, R29, R37, R38, R40, R44, R45, R46: 3.3k; R_0805_2012Metric
R21, R32, R34, R36: 4.7k; R_0805_2012Metric
R41, R42, R43, R49, R50: 150; R_0805_2012Metric
R47: 150 1%; R_0805_2012Metric
R48: 2.32k 1%; R_0805_2012Metric
RV1: Varistor; WE_VS_Varistor; MPN 82551250
TP1, TP4, TP5, TP6, TP7: DNI; TestPoint_THTPad_D1.5mm_Drill0.7mm
U2: TPD2E2U06; SOT-553; MPN TPD2E2U06DRLR; Farnell 3116500
U3: LPC11U37FBD48-401_; LQFP-48_7x7mm_P0.5mm; MPN LPC11U37FBD48/401; Farnell 2115662
U4: MCP1825S-3302E; SOT-223-3_TabPin2; MPN MCP1825S-3302E; Farnell 1578404
U5: S24SE05004PDFA_DC-DC; DCDC-5V_S24SE05004PDFA; MPN S24SE05004PDFA; Mouser 108-S24SE05004PDFA
U6, U15: MCP4725; SOT-23-6; MPN MCP4725A1T-E/CH; Farnell 2774927
U7, U13, U14: ITS4142NHUMA1; SOT-223; MPN ITS4142NHUMA1
U16: LD1086DTTR; TO-252-2; MPN LD1086DTTR (adjustable)
Y1: 12MHz; Crystal_SMD_3225-4Pin_3.2x2.5mm; MPN 7M-12.000MEEQ-T; Farnell 2308719

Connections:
+3V3: C2.1, C3.1, C4.1, C25.1, C49.1, C52.1, FB2.2, J15.18, J15.20, J16.1 (VTref), Q1.2 (G), Q1.5 (G), R3.2, R15.1, R23.2, R35.2, R37.2, R39.2, R41.2, R44.2, TP5.1, U3.8 (VDD), U3.44 (VDD), U4.3 (VO); also elsewhere on the board
+5V: C1.1, C11.1, C13.1, C16.1, C23.1, C28.1, C29.1, J6.5, J9.2 (5V), J9.4 (5V), R7.2, R45.2, R46.2, TP1.1, U4.1 (VI), U5.6 (+VOUT), U6.3 (VDD), U15.3 (VDD), U15.6 (A0); also elsewhere on the board
+24V: C14.1, C18.1, C22.1, C24.1, C26.1, C41.1, C42.1, C44.1, D3.1 (K), FB1.2, J8.5, J11.5, R6.2, R11.2, TP4.1, U5.1 (+VIN), U7.4 (IN), U13.4 (IN), U14.4 (IN)
/24_CHOKE: C47.1, D3.2 (A), FL1.4
/A_MFC_FEEDBACK_AIR: C40.1, R31.1, R33.2, TP7.1, U3.35 (PIO0_14)
/A_MFC_FEEDBACK_O2: C20.1, R10.1, R14.2, TP6.1, U3.34 (PIO0_13)
/A_MFC_PRESSURE: U3.33 (PIO0_12); also elsewhere on the board
/A_PSENSE_3: U3.32 (PIO0_11); also elsewhere on the board
/BATT_LEVEL: C43.1, R11.1, R24.2, U3.42 (PIO0_23)
/EXHALE_PWM: R34.2, U3.30 (PIO0_22), U13.3 (ON)
/EXHALE_VALVE: C17.1, D1.1 (K), J13.2, R38.2, U13.1 (OUT)
/EXTRA_PWM: R32.2, U3.36 (PIO1_13), U7.3 (ON)
/EXTRA_VALVE: C27.1, D11.1 (K), J4.2, R19.2, U7.1 (OUT)
/FLOW_I2C_SCL: J2.3, J7.3, R49.1
/FLOW_I2C_SDA: J2.4, J7.4, R50.2
/I2C_3V3_SCL: Q1.1 (S), R37.1, R49.2, U3.15 (PIO0_4)
/I2C_3V3_SDA: Q1.4 (S), R44.1, R50.1, U3.16 (PIO0_5)
/I2C_5V_SCL: Q1.6 (D), R45.1, U6.5 (SCL), U15.5 (SCL)
/I2C_5V_SDA: Q1.3 (D), R46.1, U6.4 (SDA), U15.4 (SDA)
/INHALE_PWM: R36.2, U3.37 (PIO1_14), U14.3 (ON)
/INHALE_VALVE: C45.1, D2.1 (K), J14.2, R40.2, U14.1 (OUT)
/LED_ERROR: R43.2, U3.17 (PIO0_21)
/LED_STATUS: R42.2, U3.18 (PIO1_23)
/MCU_DM: R5.2, U3.19 (USB_DM)
/MCU_DP: R4.2, U3.20 (USB_DP)
/MCU_IO_1: J15.16, U3.40 (PIO0_16)
/MCU_IO_2: J15.14, U3.26 (PIO1_21)
/MCU_IO_3: J15.12, U3.25 (PIO1_31)
/MCU_IO_4: J15.10, U3.24 (PIO1_28)
/MFC_SETPOINT_AIR: J11.3, U15.1 (VOUT)
/MFC_SETPOINT_O2: J8.3, U6.1 (VOUT)
/POWER_STATUS_DISCHARGING: C15.1, R12.2, U3.22 (PIO0_6)
/POWER_STATUS_FAIL: C50.1, R22.2, U3.23 (PIO0_7)
/PSENSE_1_DATA_READY: U3.48 (PIO1_16); also elsewhere on the board
/PSENSE_1_SPI_~CS~: U3.2 (PIO1_19); also elsewhere on the board
/PSENSE_2_DATA_READY: U3.43 (PIO1_15); also elsewhere on the board
/PSENSE_2_SPI_~CS~: U3.38 (PIO1_22); also elsewhere on the board
/PSENSE_RESET: U3.13 (PIO1_20); also elsewhere on the board
/PSENSE_SPI_CLK: U3.31 (PIO1_29); also elsewhere on the board
/PSENSE_SPI_MISO: U3.27 (PIO0_8); also elsewhere on the board
/PSENSE_SPI_MOSI: U3.28 (PIO0_9); also elsewhere on the board
/PWR+: C46.1, D4.2 (A2), FL1.2, J5.2, RV1.1
/PWR-: C46.2, D4.1 (A1), FL1.1, J5.1, RV1.2
/RPI_IO_1: J9.38 (GPIO20/MOSI1), J15.4
/RPI_IO_2: J9.37 (GPIO26), J15.2
/RPI_ON_OFF: J9.5 (SCL/GPIO3), U3.45 (PIO0_17)
/RPI_RX: J9.10 (GPIO15/RXD), R17.2
/RPI_TX: J9.8 (GPIO14/TXD), R16.2
/RPI_~ISP~: J9.11 (GPIO17), R9.2
/RPI_~RST~: J9.36 (GPIO16), R8.2
/SWCLK: J16.4 (SWDCLK/TCK), U3.29 (PIO0_10)
/SWDIO: J16.2 (SWDIO/TMS), U3.39 (PIO0_15)
/UART_RX: J10.4, R16.1, U3.46 (PIO0_18)
/UART_TX: J10.5, R17.1, U3.47 (PIO0_19)
/UPS_3V3_PU: J5.3, R23.1
/UPS_DISCHG: J5.4, R12.1
/UPS_FAIL: J5.5, R22.1
/USB_DN: J1.2 (D-), R5.1, U2.2 (NC), U2.5
/USB_DP: J1.3 (D+), R3.1, R4.1, U2.3
/USB_VBUS: J1.1 (VBUS), R21.2, U3.14 (PIO0_3)
/USER_SWITCH: C21.1, R18.2, U3.21 (PIO1_24)
/V_flow_3v3: C48.1, C53.1, C54.1, FB2.1, J2.6, J7.6
/V_flow_heater: C38.1, C39.1, C51.1, J2.1, J7.1, R47.2, U16.2 (OUT)
/XTAL_IN: C10.1, U3.6 (XTALIN), Y1.1
/XTAL_OUT: C12.1, U3.7 (XTALOUT), Y1.3
/~ISP~: J15.6, R9.1, R35.1, U3.4 (PIO0_1)
/~RESET~: C7.1, J15.8, J16.10 (~RESET~), R8.1, R39.1, U3.3 (PIO0_0)
GND: C1.2, C2.2, C3.2, C4.2, C7.2, C10.2, C11.2, C12.2, C13.2, C14.2, C15.2, C16.2, C17.2, C18.2, C19.2, C20.2, C21.2, C22.2, C23.2, C24.2, C25.2, C26.2, C27.2, C28.2, C29.2, C38.2, C39.2, C40.2, C41.2, C42.2, C43.2, C44.2, C45.2, C47.2, C48.2, C49.2, C50.2, C51.2, C52.2, C53.2, C54.2, D1.2 (A), D2.2 (A), D5.1 (K), D6.1 (K), D7.1 (K), D8.1 (K), D9.1 (K), D10.1 (K), D11.2 (A), FL1.3, H1.1, H2.1, H3.1, H7.1, J1.5 (GND), J1.6 (Shield), J2.2, J2.5, J2.MP (MountPin), J3.1, J4.1, J6.1, J7.2, J7.5, J7.MP (MountPin), J8.1, J8.4, J9.6 (GND), J9.9 (GND), J9.14 (GND), J9.20 (GND), J9.25 (GND), J9.30 (GND), J9.34 (GND), J9.39 (GND), J10.1, J11.1, J11.4, J13.1, J14.1, J15.1, J15.3, J15.5, J15.7, J15.9, J15.11, J15.13, J15.15, J15.17, J15.19, J16.3 (GND), J16.5 (GND), J16.9 (GNDDetect), R14.1, R21.1, R24.1, R29.1, R30.1, R32.1, R33.1, R34.1, R36.1, R48.1, U2.4, U3.5 (VSS), U3.9 (PIO0_20), U3.41 (VSS), U4.2 (GND), U5.2 (-VIN), U5.4 (-VOUT), U6.2 (VSS), U6.6 (A0), U7.2 (GND), U13.2 (GND), U14.2 (GND), U15.2 (VSS), Y1.2, Y1.4; also elsewhere on the board
unnamed: C19.1, FB1.1, U16.3 (IN)
unnamed: D5.2 (A), R19.1
unnamed: D6.2 (A), R38.1
unnamed: D7.2 (A), R40.1
unnamed: D8.2 (A), R41.1
unnamed: D9.2 (A), R42.1
unnamed: D10.2 (A), R43.1
unnamed: J3.2, R15.2, R18.1
unnamed: J8.2, R10.2
unnamed: J11.2, R31.2
unnamed: R6.1, R29.2, U5.3 (ON_OFF)
unnamed: R7.1, R30.2, U5.5 (TRIM)
unnamed: R47.1, R48.2, U16.1 (ADJ/GND)

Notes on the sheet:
5V header for RPI display
5V -> 3.3V
24VDC 4A
24V -> 5V 3A
24V power input
Power
Pressure sensor(s)
optional output voltage trim
3x 24V Valve
Input filter + reverse polarity protection
Required: - 12-24V 6W 50mv rms - 3.3V 25mv rms
3.3V -1%/+5% 50mA 20mv rms
Valves are driven with 24V PWM signal
Place close to ADC input
2x Mass Flow Controller
2x Flow Sensor
RPI Connector
Signal will be connected by UPS relay Series resistor for robustness + filtering
TODO SETPOINT_OUT robustness: ESD/SURGE PROTECTION?
Strong pulldown: overrule mcu internal pullups to avoid glitch at power-on
SCK1
MOSI_1
MISO_1
SCK0
MISO_0
MOSI_0
adc
Extra I/O
Power / status LEDS
Should be compatible with TTL-232R-3V3 Note: are TX/RX correct?
CT16B0_MAT0
CT16B1_MAT1
CT16B0_MAT1
RPI mounting
Debug: SWD + UART
ADC
USB
(reset)
(boot_USB)
(boot_~ISP~)

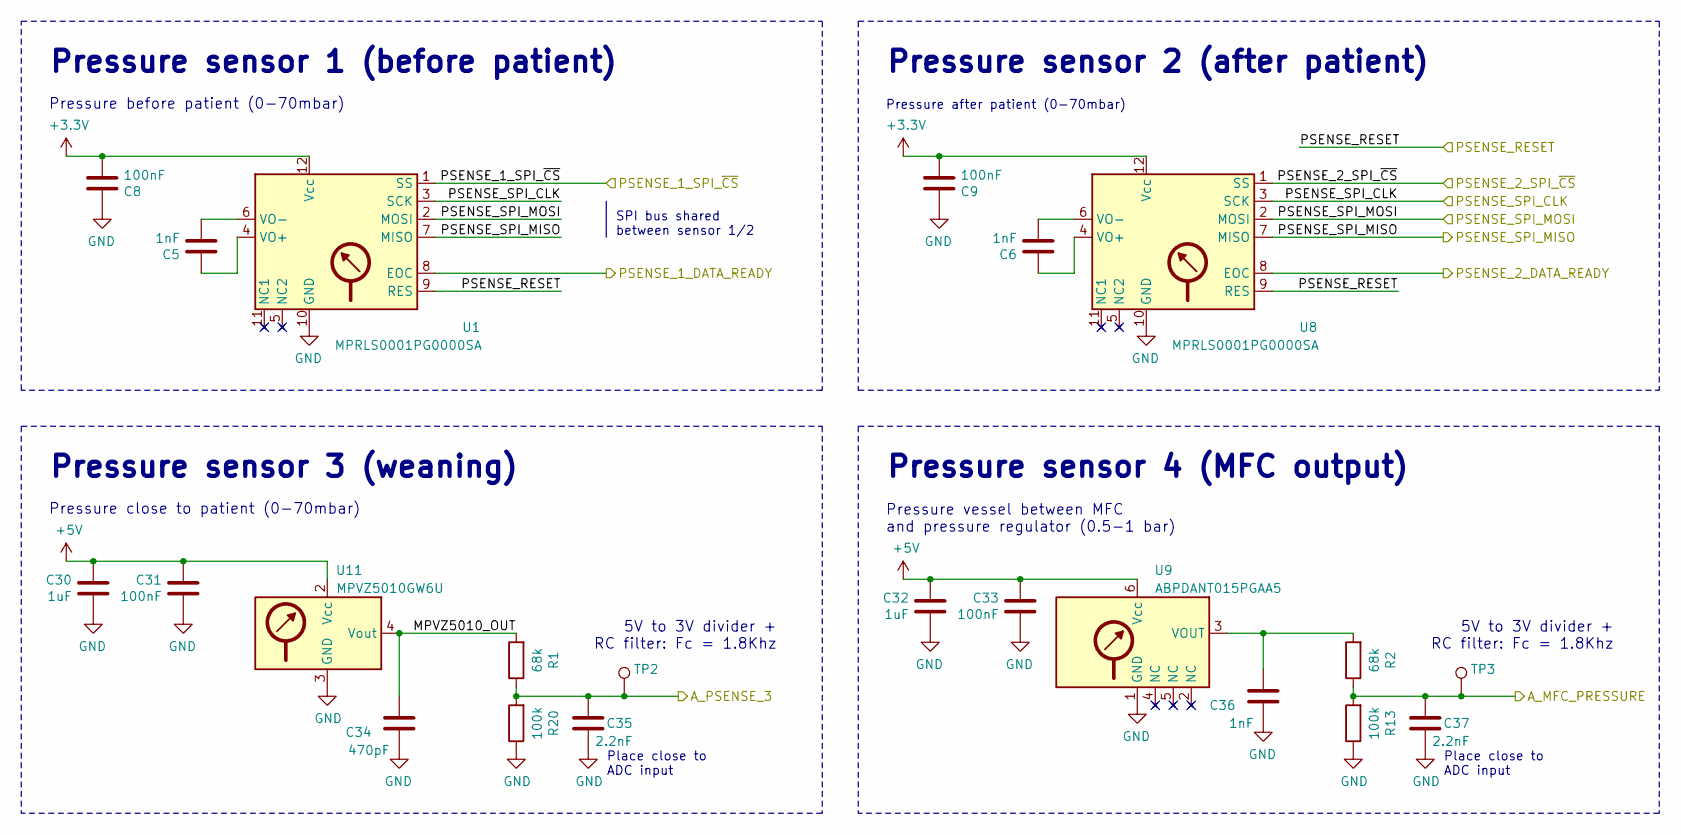
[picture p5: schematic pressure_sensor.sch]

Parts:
C5, C6, C36: 1nF; C_0805_2012Metric
C8, C9, C31, C33: 100nF; C_0805_2012Metric
C30, C32: 1uF; C_0805_2012Metric
C34: 470pF; C_0805_2012Metric
C35, C37: 2.2nF; C_0805_2012Metric
R1, R2: 68k; R_0805_2012Metric
R13, R20: 100k; R_0805_2012Metric
TP2, TP3: DNI; TestPoint_THTPad_D1.5mm_Drill0.7mm
U1, U8: MPRLS0001PG0000SA; MPN MPRLS0001PG0000SA; Digikey 480-7100-1-ND
U9: ABPDXXX000XXAX5; ABPDXXX000XX0XX; MPN ABPDANT015PGAA5; Digikey 480-6253-ND
U11: MPVZ5010GW6U; MPN MPVZ5010GW6U

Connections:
+3V3: C8.2, C9.2, U1.12 (Vcc), U8.12 (Vcc); also elsewhere on the board
+5V: C30.1, C31.1, C32.1, C33.1, U9.6 (Vcc), U11.2 (Vcc); also elsewhere on the board
/A_MFC_PRESSURE: C37.1, R2.1, R13.2, TP3.1; also elsewhere on the board
/A_PSENSE_3: C35.1, R1.1, R20.2, TP2.1; also elsewhere on the board
/PSENSE_1_DATA_READY: U1.8 (EOC); also elsewhere on the board
/PSENSE_1_SPI_~CS~: U1.1 (SS); also elsewhere on the board
/PSENSE_2_DATA_READY: U8.8 (EOC); also elsewhere on the board
/PSENSE_2_SPI_~CS~: U8.1 (SS); also elsewhere on the board
/PSENSE_RESET: U1.9 (RES), U8.9 (RES); also elsewhere on the board
/PSENSE_SPI_CLK: U1.3 (SCK), U8.3 (SCK); also elsewhere on the board
/PSENSE_SPI_MISO: U1.7 (MISO), U8.7 (MISO); also elsewhere on the board
/PSENSE_SPI_MOSI: U1.2 (MOSI), U8.2 (MOSI); also elsewhere on the board
/pressure_sensor/MPVZ5010_OUT: C34.1, R1.2, U11.4 (Vout)
GND: C8.1, C9.1, C30.2, C31.2, C32.2, C33.2, C34.2, C35.2, C36.2, C37.2, R13.1, R20.1, U1.10 (GND), U8.10 (GND), U9.1 (GND), U11.3 (GND); also elsewhere on the board
unnamed: C5.1, U1.4 (VO+)
unnamed: C5.2, U1.6 (VO-)
unnamed: C6.1, U8.4 (VO+)
unnamed: C6.2, U8.6 (VO-)
unnamed: C36.1, R2.2, U9.3 (VOUT)

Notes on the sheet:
Pressure after patient (0-70mbar)
Pressure before patient (0-70mbar)
Pressure sensor 2 (after patient)
Pressure sensor 1 (before patient)
SPI bus shared between sensor 1/2
Pressure sensor 3 (weaning)
Pressure close to patient (0-70mbar)
Place close to ADC input
5V to 3V divider + RC filter: Fc = 1.8Khz
Pressure vessel between MFC and pressure regulator (0.5-1 bar)
Pressure sensor 4 (MFC output)

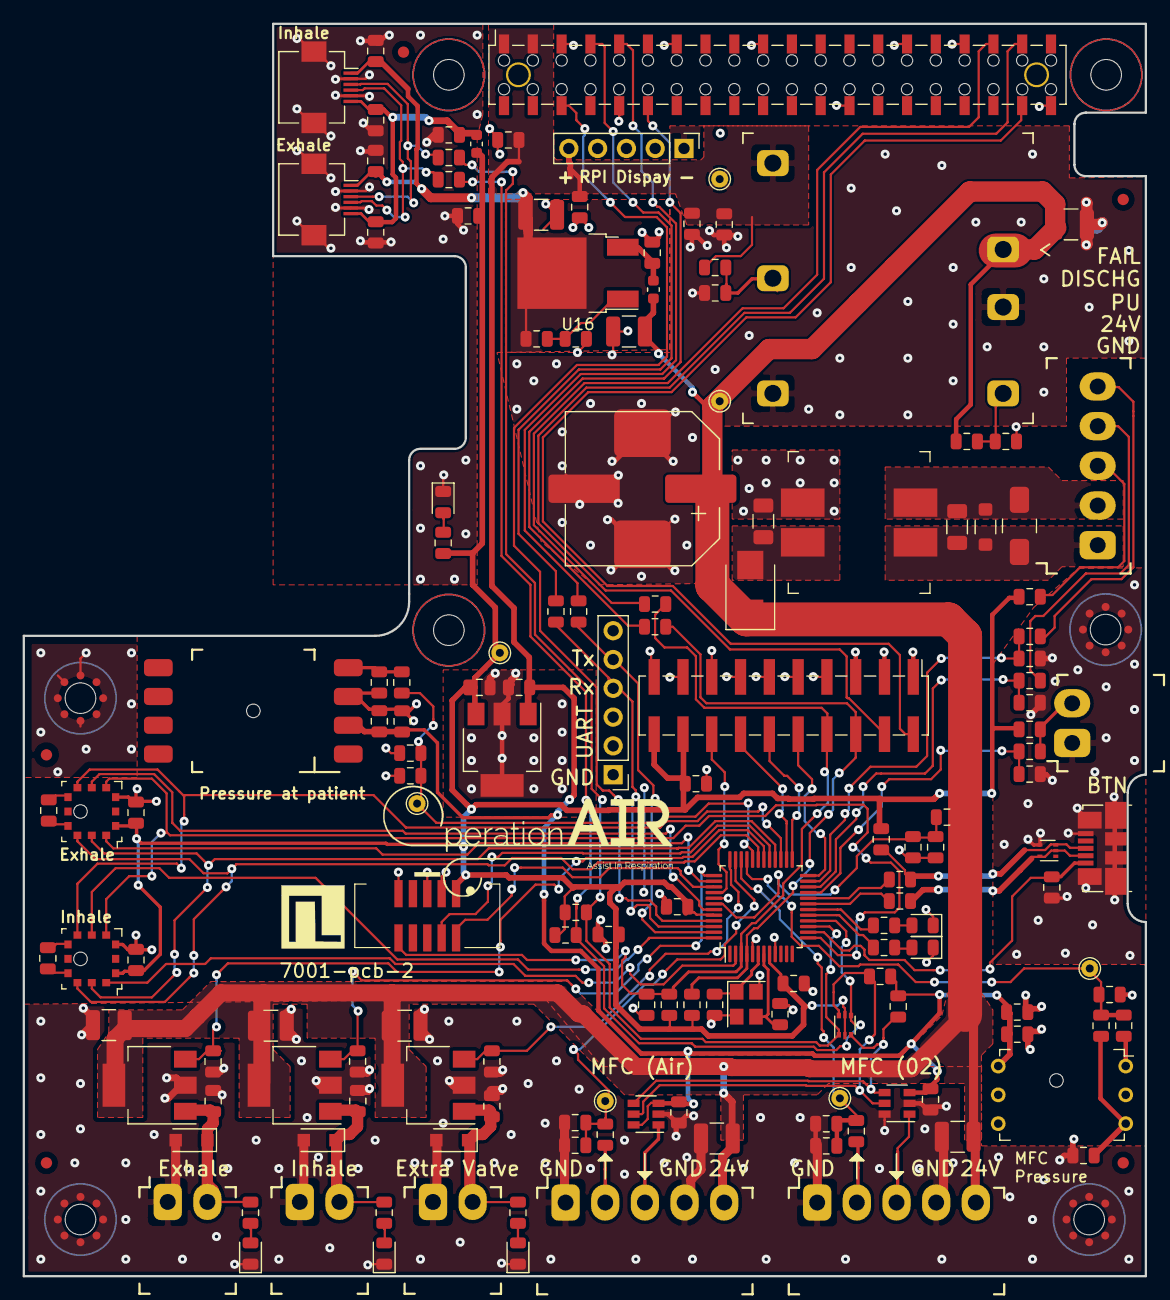
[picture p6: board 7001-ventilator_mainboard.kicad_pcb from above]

Board: 2 copper layers, 99.0 x 110.5 mm, 167 parts (0 on the bottom side), 87 nets.

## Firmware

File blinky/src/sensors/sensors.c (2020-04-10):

#include <lpc_tools/boardconfig.h>
#include <lpc_tools/GPIO_HAL.h>
#include <c_utils/max.h>

#include "sensors.h"
#include "calculated.h"
#include "actuators/control_signals.h"
#include "ADC.h"
#include "flow.h"
#include "breathing.h"

#include "MPRLS_pressure.h"
#include "board_config/board_GPIO_ID.h"

#include "global_settings.h"

struct {
    int32_t pressure_MFC;
    int32_t pressure_in;
    int32_t pressure_out;
    int32_t pressure_patient;

    int32_t flow_MFC_air;
    int32_t flow_MFC_O2;

    int32_t battery_level;

    int32_t flow_out; //SCCPM

    int32_t inspiratory_hold_result;

    int32_t expiratory_hold_result;
} Sensors;

static bool g_error = false;
static bool g_error_flow = false;
static bool g_error_mprls_out = false;
static bool g_error_mprls_in = false;

static int32_t g_offset_pressure_in = 0;
static int32_t g_offset_pressure_out = 0;

// See schematics
#define ADC_FACTOR_PRESSURE             (168.0/100.0)
#define ADC_FACTOR_FLOW_MFC             (168.0/100.0)
#define ADC_FACTOR_BATTERY              (11.5/1.5)

// TODO FIXME: voltage divider for flow/MFC input is be wrong!
// Datasheet table shows 1-5V instead of assumed 0-12!!
#define ADC_FACTOR_PRESSURE_MFC         (13.3/3.3)
#define ADC_FACTOR_PREG_PRESSURE        (1.0)

// Slew rate limits (in app ticks / full ADC range)
// Tweak these to limit noise spikes.
// 1 = lowest value (effectively no filtering)
// 1024 (ADC_RANGE) = highest value (strong filter)
#define SLEW_LIMIT_PRESSURE_MFC             (10)
#define SLEW_LIMIT_PRESSURE                 (5)
#define SLEW_LIMIT_PREG_PRESSURE            (400)
#define SLEW_LIMIT_MFC_FEEDBACK             (50)
#define SLEW_LIMIT_BATTERY_LEVEL            (500)


static MPRLS mprls1;
static MPRLS mprls2;

void sensors_init(void) {

    UPS_status_init();
    calculated_init();

    mprls_init(&mprls1, LPC_SSP0,
        board_get_GPIO(GPIO_ID_PSENSE_1_CS),
        board_get_GPIO(GPIO_ID_PSENSE_1_DRDY),
        board_get_GPIO(GPIO_ID_PSENSE_RESET));

    mprls_init(&mprls2, LPC_SSP0,
        board_get_GPIO(GPIO_ID_PSENSE_2_CS),
        board_get_GPIO(GPIO_ID_PSENSE_2_DRDY),
        board_get_GPIO(GPIO_ID_PSENSE_RESET));

    mprls_enable(&mprls1);
    mprls_enable(&mprls2);

    ADC_init();

    if (I2C_PULL_UP_AVAILABLE) {
        if(!flowsensor_enable()) {
            g_error_flow = true;
        }
    }

    sensors_reset();
}

bool sensors_calibrate_offset(void)
{
    // reset offsets to zero. This is done because we dont
    // want the sensors_read_XXX() calls below to include any previous offset.
    g_offset_pressure_in = 0;
    g_offset_pressure_out = 0;

    g_offset_pressure_in = sensors_read_pressure_insp_pa();
    g_offset_pressure_out = sensors_read_pressure_exp_pa();

    return true; //todo g_error;
}

void sensors_reset(void)
{
    g_error = false;
    g_error_flow = false;
    g_error_mprls_out = true;
    g_error_mprls_in = true;

    Sensors.pressure_MFC = -1;
    Sensors.pressure_in = -1;
    Sensors.pressure_out = -1;
    Sensors.pressure_patient = -1;

    Sensors.flow_out = -1;
    Sensors.flow_MFC_O2 = -1;
    Sensors.flow_MFC_air = -1;
    Sensors.battery_level = 0;

    g_offset_pressure_in = 0;
    g_offset_pressure_out = 0;

    sensors_update(1);
}

static void filter_adc(int32_t* state, enum ADC_ID ID, int32_t slew_limit)
{
    const int32_t prev = *state;
    int32_t delta = (int32_t)ADC_read(ID) - prev;

    if(prev >= 0) {
        // Cap delta to +/- slew_limit unless it is the first sample since reset
        delta = max(min(delta, slew_limit),(-1*slew_limit));
    }
    *state+= delta;
}


static void _update_sensor_in(void)
{
    // sample sensor1
    if(mprls_is_ready(&mprls1)) {
        // read value and trigger next sample
        Sensors.pressure_in = mprls_read_data(&mprls1);
        mprls_trigger_read(&mprls1);

    } else if(mprls_is_timeout(&mprls1)) {

        // Timeout! try to trigger next sample, but something is wrong here!
        // TODO handle error

        g_error_mprls_in = true;
        mprls_trigger_read(&mprls1);
    }
}

static void _update_sensor_out(void)
{
    // sample sensor2
    if(mprls_is_ready(&mprls2)) {
        // read value and trigger next sample
        Sensors.pressure_out = mprls_read_data(&mprls2);
        mprls_trigger_read(&mprls2);

    } else if(mprls_is_timeout(&mprls2)) {

        // Timeout! try to trigger next sample, but something is wrong here!
        // TODO handle error

        g_error_mprls_out = true;
        mprls_trigger_read(&mprls2);
    }
}


static uint32_t count = 0;
void sensors_update(unsigned int dt)
{
    filter_adc(&Sensors.pressure_MFC, ADC_ID_PRESSURE_MFC,
            ADC_RANGE/SLEW_LIMIT_PRESSURE_MFC);

    if (I2C_PULL_UP_AVAILABLE) {
        if (count++ % 5 == 0) {
            // calculate flow in SLPM
            float flow_SLPM = read_flow_sensor();
            flow_SLPM = flow_SLPM*3.14f*(0.015f/2)*(0.015f/2)*1000*60;

            // SLPM to SCCPM
            Sensors.flow_out = 1000*flow_SLPM;
        }
    }

    _update_sensor_in();
    _update_sensor_out();


    filter_adc(&Sensors.flow_MFC_O2, ADC_ID_MFC_O2,
            ADC_RANGE/SLEW_LIMIT_MFC_FEEDBACK);
    filter_adc(&Sensors.flow_MFC_air, ADC_ID_MFC_AIR,
            ADC_RANGE/SLEW_LIMIT_MFC_FEEDBACK);

    if(board_has_ADC(ADC_ID_BATTERY_LEVEL)) {
        filter_adc(&Sensors.battery_level, ADC_ID_BATTERY_LEVEL,
                ADC_RANGE/SLEW_LIMIT_BATTERY_LEVEL);
    }


    if(board_has_ADC(ADC_ID_PRESSURE_PATIENT)) {
        filter_adc(&Sensors.pressure_patient, ADC_ID_PRESSURE_PATIENT,
                ADC_RANGE/SLEW_LIMIT_PRESSURE);
    }

    Sensors.inspiratory_hold_result = (int32_t)breathing_get_inspiratory_hold_result();
    Sensors.expiratory_hold_result = (int32_t)breathing_get_expiratory_hold_result();
}

static float p_MFC_pa;
int32_t sensors_read_pressure_MFC_pa(void)
{
    const int p_mv = ADC_scale(Sensors.pressure_MFC, ADC_FACTOR_PRESSURE_MFC);

    // calibrated 10-4-2020 expirementally
    p_MFC_pa = (0.9 * p_MFC_pa) + (0.1 * (16.56 * p_mv + 21523));

    return p_MFC_pa;

}

// Virtual 'sensor' that returns the current setpoint
#include "breathing.h"
int32_t sensors_read_pressure_target_pa(void)
{
    return breathing_read_setpoint_pa();
}

int32_t sensors_read_pressure_insp_pa(void)
{
    int32_t result = 0;
    result = Sensors.pressure_in;

    return result - g_offset_pressure_in;
}

int32_t sensors_read_pressure_exp_pa(void)
{
    int32_t result = 0;
    result = Sensors.pressure_out;

    return result - g_offset_pressure_out;
}

int32_t sensors_read_pressure_patient_pa(void)
{
    const int v_pressure = ADC_scale(Sensors.pressure_patient, ADC_FACTOR_PRESSURE);

    // NOTE: this is calibrated experimentally, instead of datasheet-based (MPVZ5010)
    const int offset_mv = 167;
    const int scale_factor = 2157;
    int32_t result = ((v_pressure-offset_mv)*scale_factor)/1000;

    return result;
}

int32_t sensors_read_flow_out_SCCPM(void)
{
    return Sensors.flow_out;
}
int32_t sensors_read_flow_in_SCCPM(void)
{
    // Flow into patient is approximated as total flow from MFCs
    return (sensors_read_flow_MFC_O2_SCCPM() + sensors_read_flow_MFC_air_SCCPM());
}

int32_t sensors_read_flow_MFC_O2_SCCPM(void)
{
    const int v_MFC_O2 = sensors_read_raw_MFC_O2_mv();
    // O-5000 mV / 100.0 = 0-50 000 SCCPM

    return v_MFC_O2 * 10;
}

int32_t sensors_read_raw_MFC_O2_mv(void)
{
    return ADC_scale(Sensors.flow_MFC_O2, ADC_FACTOR_FLOW_MFC);
}
int32_t sensors_read_raw_MFC_air_mv(void)
{
    return ADC_scale(Sensors.flow_MFC_air, ADC_FACTOR_FLOW_MFC);
}


int32_t sensors_read_flow_MFC_air_SCCPM(void)
{
    const int v_MFC_air = sensors_read_raw_MFC_air_mv();
    // O-5000 mV / 100.0 = 0-50 000 SCCPM

    return v_MFC_air * 10;
}

int32_t sensors_read_flow_out_avg_SCCPM(void)
{
    return calculated_flow_out_avg_SCCPM();
}


/**
 * Calculated 'sensors': based on one or more other sensor values.
 * See calculated.c for implementation
 */

int32_t sensors_read_volume_realtime_MFC_O2_CC(void)
{
    return calculated_volume_realtime_MFC_O2_CC();
}
int32_t sensors_read_volume_realtime_MFC_air_CC(void)
{
    return calculated_volume_realtime_MFC_air_CC();
}
int32_t sensors_read_volume_realtime_in_CC(void)
{
    return calculated_volume_realtime_in_CC();
}
int32_t sensors_read_volume_realtime_out_CC(void)
{
    return calculated_volume_realtime_out_CC();
}

int32_t sensors_read_oxygen_percent(void)
{
    return calculated_oxygen_percent();
}

int32_t sensors_read_volume_cycle_in_CC(void)
{
    return calculated_volume_in_CC();
}
int32_t sensors_read_volume_cycle_out_CC(void)
{
    return calculated_volume_out_CC();
}

int32_t sensors_get_inspiratory_hold_result()
{
    return Sensors.inspiratory_hold_result;
}

int32_t sensors_get_expiratory_hold_result()
{
    return Sensors.expiratory_hold_result;
}

enum UPSStatus sensors_read_UPS_status(void)
{
    return UPS_status_get();
}

uint32_t sensors_read_UPS_voltage_mv(void)
{
    return ADC_scale(Sensors.battery_level, ADC_FACTOR_BATTERY);
}



void sensors_read_all(SensorsAllData *data)
{
    data->flow_inhale = sensors_read_flow_in_SCCPM();
    data->flow_exhale = sensors_read_flow_out_SCCPM();

    data->pressure_inhale = sensors_read_pressure_insp_pa();
    data->pressure_exhale = sensors_read_pressure_exp_pa();
    data->pressure_patient = sensors_read_pressure_patient_pa();
    data->pressure_mfc = sensors_read_pressure_MFC_pa();

    data->oxygen = sensors_read_oxygen_percent();
    data->tidal_volume_exhale = sensors_read_volume_cycle_out_CC();
    data->tidal_volume_inhale = sensors_read_volume_cycle_in_CC();

    data->minute_volume = sensors_read_flow_out_avg_SCCPM();

    data->cycle_state = breathing_get_cycle_state();
    data->power_status = (sensors_read_UPS_status()
            | sensors_read_UPS_voltage_mv());

    data->inspiratory_hold_result = sensors_get_inspiratory_hold_result();
    data->expiratory_hold_result = sensors_get_expiratory_hold_result();
}

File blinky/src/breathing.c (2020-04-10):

#include <c_utils/assert.h>
#include <c_utils/max.h>
#include <c_utils/constrain.h>

#include "actuators/control_signals.h"
#include "sensors/sensors.h"
#include "sensors/calculated.h"

#include "global_settings.h"
#include "breathing.h"
#include "log.h"
#include "app.h"

#include <math.h>
#include <stdlib.h>

#include "cmsis_dsp_lib/arm_math.h"


static bool program_validation(void);

// PID loop for DPR
float DPR_PID_Kp = 1.4; //1
float DPR_PID_Ki = 0.01; //0.1
float DPR_PID_Kd = 0.25; //3.0

static int g_signal_to_switch = 0;
static volatile int g_pressure_setpoint_pa = 0;
static arm_pid_instance_f32 DPR_PID;    // pressure regulator
static arm_pid_instance_f32 MFC_PID;    // mass flow controllers
static arm_pid_instance_f32 EXP_PID;

static float g_pressure_state_insp = 0;
static float g_pressure_state_exp = 0;
static float g_pressure_system_pa = 0;
static float g_MFC_pressure_pa = 0;

static float g_to_DPR = 0;
static float g_to_EXP = 0;

static float g_inspiratory_hold_result = 0;
static float g_expiratory_hold_result = 0;

static volatile enum BreathCycleState g_breath_cycle_state = BreathCycleStateNone;

// PID loop for MFC
float MFC_PID_Kp = 3.0;
float MFC_PID_Ki = 0.0;
float MFC_PID_Kd = 0.5;

// PID loop for EXP
float EXP_PID_Kp = 3;
float EXP_PID_Ki = 0;
float EXP_PID_Kd = 10;

#define CLOSE_TIME_MS 4000

#define MFC_FLOW_MIN_SLPM   0.0

// TODO 50
#define MFC_FLOW_MAX_SLPM   50.0

const int g_MFC_setpoint_pa = 65000;


int breathing_read_setpoint_pa(void)
{
    return g_pressure_setpoint_pa;
}

void breathing_print_DPR_PID(void)
{
    log_debug("DPR PID: %d, %d, %d",
            (int)DPR_PID_Kp,
            (int)DPR_PID_Ki,
            (int)DPR_PID_Kd);
}
void breathing_print_MFC_PID(void)
{
    log_debug("MFC PID: %d, %d, %d",
            (int)MFC_PID_Kp,
            (int)MFC_PID_Ki,
            (int)MFC_PID_Kd);
}
void breathing_print_EXP_PID(void)
{
    log_debug("EXP PID: %d, %d, %d",
              (int)EXP_PID_Kp,
              (int)EXP_PID_Ki,
              (int)EXP_PID_Kd);
}

static void _init_DPR_PID(void)
{
    // Begin PID

    arm_pid_reset_f32(&DPR_PID);
    DPR_PID.Kp = DPR_PID_Kp;
    DPR_PID.Ki = DPR_PID_Ki;
    DPR_PID.Kd = DPR_PID_Kd;
    // init calculates the required coefficients based on the PID input
    // A0 = Kp + Ki + Kd
    // A1 = (-Kp ) - (2 * Kd )
    // A2 = Kd
    // The PID controller calculates the following transfer function
    // y[n] = y[n-1] + A0 * x[n] + A1 * x[n-1] + A2 * x[n-2]
    arm_pid_init_f32(&DPR_PID, 1);
}
static void _init_MFC_PID(void)
{
    // Begin PID

    arm_pid_reset_f32(&MFC_PID);
    MFC_PID.Kp = MFC_PID_Kp;
    MFC_PID.Ki = MFC_PID_Ki;
    MFC_PID.Kd = MFC_PID_Kd;
    // init calculates the required coefficients based on the PID input
    // A0 = Kp + Ki + Kd
    // A1 = (-Kp ) - (2 * Kd )
    // A2 = Kd
    // The PID controller calculates the following transfer function
    // y[n] = y[n-1] + A0 * x[n] + A1 * x[n-1] + A2 * x[n-2]
    arm_pid_init_f32(&MFC_PID, 1);
}

static void _init_EXP_PID(void)
{
    // Begin PID
    arm_pid_reset_f32(&EXP_PID);
    EXP_PID.Kp = EXP_PID_Kp;
    EXP_PID.Ki = EXP_PID_Ki;
    EXP_PID.Kd = EXP_PID_Kd;

    arm_pid_init_f32(&EXP_PID, 1);
}

void breathing_tune_DPR_PID(float kp, float ki, float kd)
{
    DPR_PID_Kp = kp;
    DPR_PID_Ki = ki;
    DPR_PID_Kd = kd;
    _init_DPR_PID();

    log_debug("DPR PID: %d, %d, %d",
            (int)DPR_PID_Kp,
            (int)DPR_PID_Ki,
            (int)DPR_PID_Kd);
}
void breathing_tune_MFC_PID(float kp, float ki, float kd)
{
    MFC_PID_Kp = kp;
    MFC_PID_Ki = ki;
    MFC_PID_Kd = kd;
    _init_MFC_PID();

    log_debug("PID: %d, %d, %d",
            (int)MFC_PID_Kp,
            (int)MFC_PID_Ki,
            (int)MFC_PID_Kd);
}

void breathing_tune_EXP_PID(float kp, float ki, float kd)
{
    EXP_PID_Kp = kp;
    EXP_PID_Ki = ki;
    EXP_PID_Kd = kd;
    _init_EXP_PID();

    log_debug("PID: %d, %d, %d",
              (int)EXP_PID_Kp,
              (int)EXP_PID_Ki,
              (int)EXP_PID_Kd);
}

static struct {
    volatile uint32_t cycle_time;
    volatile uint32_t breathing_time;
    volatile uint32_t hold_time;
    volatile uint32_t timestamp_start_close;
    volatile bool breathing_cycle_finished;
} breathing;


bool breathing_init(void)
{
    if (!program_validation()) {
        return false;
    }

    return true;
}

void breathing_start_calibration(void)
{
    // open Valve: startup auto-calibrate requires 0psi pressure in the system
    control_valve_exp_on(10000);
}
void breathing_finish_calibration(void)
{
    sensors_calibrate_offset();
}
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

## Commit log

2020-03-21 First start of schematic design
    [7001-ventilator_mainboard.kicad_pcb, 7001-ventilator_mainboard.sch]
2020-03-21 Cleanup first design
    [7001-ventilator_mainboard.sch]
2020-03-21 Add 0-20mA for pressure regulator
    The pressure regulator can be adjusted via 4-20mA (SPI via AD5410)
    The regulator has an on-board pressure sensor giving 4-20mA feedback, which
    we convert to 0.6-3.0V for the ADC.
    [7001-ventilator_mainboard.kicad_pcb, 7001-ventilator_mainboard.sch]
2020-03-22 Schematics: add RPI hat, refactor power section
    [7001-ventilator_mainboard.sch]
2020-03-22 Schematics: add pressure sensors
    The design allows 2 pressure sensors: 'sensor 1' and 'sensor 2'.
    Only sensor 1 is required. Sensor 2 can be left out, but may be placed in case of
    changing requirements in the future (e.g. using 2 sensors to measure
    flow).
    Each of the sensors may be implemented by choosing one of 3 different footprints.
    On the PCB layout, these 3 footprints will be overlapped to create a
    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
    [7001-ventilator_mainboard.kicad_pcb, 7001-ventilator_mainboard.sch, pressure_sensor.sch]
2020-03-22 Schematics/PCB: add screw terminal footprints
    [7001-ventilator_mainboard.kicad_pcb, 7001-ventilator_mainboard.sch]
2020-03-22 Schematics/PCB: mounting holes, group components in layout
    [7001-ventilator_mainboard.kicad_pcb, 7001-ventilator_mainboard.sch]
2020-03-23 Schematics: add 24v,12v power supplies, etc
    [7001-ventilator_mainboard.kicad_pcb, 7001-ventilator_mainboard.sch, pressure_sensor.sch]
2020-03-23 schematics: ready for review?
    [7001-ventilator_mainboard.kicad_pcb, 7001-ventilator_mainboard.sch, 7001-ventilator_mainboard.xlsx]
2020-03-23 update bom with ordernumbers
    [7001-ventilator_mainboard.xlsx]
2020-03-23 Cleanup BOM, sync with schematic, prepare layout
    [7001-ventilator_mainboard.kicad_pcb, 7001-ventilator_mainboard.sch, 7001-ventilator_mainboard.xlsx, pressure_sensor.sch]
2020-03-24 Add non-pcb parts (connector mating parts) to BOM
    [7001-ventilator_mainboard.xlsx]
2020-03-24 update schematics from feedback
    [7001-ventilator_mainboard.sch]
2020-03-24 Update schematics based on more feedback
    [7001-ventilator_mainboard.sch, pressure_sensor.sch]
2020-03-24 Add 10-pin SWD connector, SMD connector for RPI
    [7001-ventilator_mainboard.sch]
2020-03-24 Sync design with BOM
    [7001-ventilator_mainboard.kicad_pcb, 7001-ventilator_mainboard.sch, 7001-ventilator_mainboard.xlsx]
2020-03-24 Finalize BOM, add all footprints
    [7001-ventilator_mainboard.kicad_pcb, 7001-ventilator_mainboard.sch, 7001-ventilator_mainboard.xlsx]
2020-03-24 PCB: Halfway layouting
    [7001-ventilator_mainboard.kicad_pcb, 7001-ventilator_mainboard.sch, pressure_sensor.sch]
2020-03-24 PCB: route bottom half
    [7001-ventilator_mainboard.kicad_pcb]
2020-03-24 update layout
    [7001-ventilator_mainboard.kicad_pcb, 7001-ventilator_mainboard.sch]
2020-03-24 layout: everything except pressure sensors
    [7001-ventilator_mainboard.kicad_pcb]
2020-03-24 Fix footprint bugs
    [7001-ventilator_mainboard.kicad_pcb, 7001-ventilator_mainboard.sch, pressure_sensor.sch]
2020-03-24 PCB: Finish layout
    [7001-ventilator_mainboard.kicad_pcb, 7001-ventilator_mainboard.sch]
2020-03-24 PCB: final BOM (1x 100nf removed)
    [7001-ventilator_mainboard.xlsx]
2020-03-25 PCB: add production files (gerber)
2020-03-25 PCB: fix board outline to allow 3d step export
    [7001-ventilator_mainboard.kicad_pcb]
2020-03-25 add settings struct
    These are the settings that will be passed down from the raspberry pi.
    This will probably change in the near future.
2020-03-25 Remove usb mass storage driver: only cdc
    [storage_strategy.xlsx]
2020-03-25 Firmware: write board_config, strip obsolete code
    [storage_strategy.xlsx]
2020-03-25 Firmware: strip more obsolete code, start implementing analog sensors
    The scale factor for the flow sensor & DPR are not entirely clear:
    - The flow sensor was assumed to be ratiometric, but the datasheet shows
    a table from 1-5V. We should probably assume the table to be correct.
    - What is the DPR range? Also, is it 0-20mA or 4-20mA?
2020-03-26 Revert "Merge 'board_config'"
    This reverts commit ff83990df67a0bb2994b00c9bb8aaf5a0e8a4da0, reversing
    changes made to 7acdfaee9a63d0f7a54f232d340b9122f2a7cf64.
2020-03-26 Write new board config
2020-03-26 board support: remove obsolete stuff
2020-03-26 board support: remove more obsolete stuff
2020-03-26 Fix board support for lpc11uxx devboard
    The devboard needs P1_24 low to enable the USB D+ pullup
2020-03-26 Add utility functions to enable status+error leds
2020-03-26 Add support for Honeywel AWM700 flow sensor (it is non-linear between 0-5V)
    The interpolation from lookup table is tested with a unit test.
    Results are in SCCPM: 1/1000 th of a SLPM
2020-03-26 Schematics: add pressure sensor datasheet
    [pressure_sensor.sch]
2020-03-27 Try to communicate with MPRLS5000 pressure sensor (SPI)
2020-03-27 Add data_ready pin for mprl driver
2020-03-27 Add reset pin to MPRL driver
2020-03-27 Add crc check for settings communication.
    Should make it generally applied to all communications, regardless of
    current command.
2020-03-27 First test demo: DPR control based on pressure
2020-03-28 Control loop fom 1khz to 500Hz
2020-03-28 Working driver for MPRLS pressure sensor (read blocking)
2020-03-28 Clean up pressure sensor branch
2020-03-28 Bugfix: cli shows sensor1 values at pressure sensor 2
2020-03-28 Fix scale factors, filter pressure sensors
2020-03-29 Update demo program: more filtering
2020-03-29 Add dpr stop function, hardcoded flow controller
2020-03-29 Add framework for requesting sensor data through uart
2020-03-29 Implement command to read all sensor data
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2020-03-31 Fix analog sensor
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2020-04-01 Pi comms/settings: fix verification, disiable LED blinking
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2020-04-03 PCB: schematics for V2
    [7001-ventilator_mainboard.kicad_pcb, 7001-ventilator_mainboard.sch, pressure_sensor.sch]
2020-04-03 PCB: update BOM
    [7001-ventilator_mainboard.xlsx]
2020-04-03 Fix bug in schematics
    [7001-ventilator_mainboard.sch]
2020-04-03 Update schematics (PSU connector) + BOM
    [7001-ventilator_mainboard.kicad_pcb, 7001-ventilator_mainboard.sch, 7001-ventilator_mainboard.xlsx]
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2020-04-03 PCB: layout in progress
    [7001-ventilator_mainboard.kicad_pcb, 7001-ventilator_mainboard.sch]
2020-04-03 PCB layout: position of components near-final
    [7001-ventilator_mainboard.kicad_pcb, 7001-ventilator_mainboard.sch]
2020-04-03 PCB layout: final locations and BOM (?)
    [7001-ventilator_mainboard.kicad_pcb, 7001-ventilator_mainboard.sch, 7001-ventilator_mainboard.xlsx]
2020-04-03 PCB layout: DRC pass
    [7001-ventilator_mainboard.kicad_pcb, 7001-ventilator_mainboard.sch]
2020-04-03 PCB: final BOM
    [7001-ventilator_mainboard.xlsx]
2020-04-03 PCB: improve silkscreen, mounting holes
    [7001-ventilator_mainboard.kicad_pcb, 7001-ventilator_mainboard.sch]
2020-04-03 PCB: minor improvements, add OperationAir logo
    [7001-ventilator_mainboard.kicad_pcb, 7001-ventilator_mainboard.sch]
2020-04-03 PCB: layout + BOM + Gerbers ready for review
    [7001-ventilator_mainboard-B_Cu.gbr, 7001-ventilator_mainboard-B_Fab.gbr, 7001-ventilator_mainboard-B_Mask.gbr, 7001-ventilator_mainboard-B_Paste.gbr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]
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2020-04-05 Fix critical bug: reading multiple elements from ringbuffer
    Reading from current read pointer is not guaranteed. Next element may be
    wrapped around to begining of the buffer.
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2020-04-06 Flow sensor sampling time fixed, diameter changed.
2020-04-07 Fix the pressure sensor saturation.
2020-04-07 Fixed the PWM names (to insp and exp valves)
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2020-04-09 Add self-test, rename insp and exp pressure sensors correctly.
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2020-04-09 Fix board config for PCB V1
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2020-04-09 Fix flow sensor includeS
2020-04-10 Calibrate MFC pressure sensor
    This calibration is approximately correct between 0.5-1 bar.
    Somehow the sensor gives a large offset at P=0.
2020-04-10 Tune expiration valve, fix expiratory hold
2020-04-10 Fix oxygen for board V1
    Oxygen / air ADC channels were swapped
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2020-04-13 Bugfix: MPRLS sensors share reset signal
    On init, only reset once
2020-04-15 Bugfix: fix error handling for flow sensor
    Flow sensor returns -1 on failure. I2C Bus errors should not be set if
    nothing goes wrong
2020-04-19 Issue #15: Update settings bounds
    The firmware rejects new settings containing values outside the valid range.
    It is important that the GUI is updated to constrain user input to the
    same updated bounds: otherwise invalid config may be created. While the MCU
    will keep the patient safe by rejecting such invalid config,
    the end-user might be confused why the settings were not applied..
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2020-04-23 Fix duration of offset calibration, boot faster
2020-04-30 Fix the Exp PID loop: reference ramp added. Add a boundary on the DPR control loop. Add some cli commands to test the valves.
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
